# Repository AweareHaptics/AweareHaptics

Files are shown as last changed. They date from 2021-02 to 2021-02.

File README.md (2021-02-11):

# AweareHaptics

Nowadays, the french population amounts more than 207 000 blind people and more than a million people suffer from visual defficiencies. According to the OMS, the number of visually impaired people should triple by 2050. Currently, the support tools developed and available for these people are not technologically advanced and often require significant purchase costs. We therefore decided to develop a tool to help with spatial orientation, accessible to all, for the blind or visually impaired.

**Aweare Haptics is an open source project on the development of a haptic vest allowing the blind or visually impaired to orient themselves in their surrounding environment.**

Aweare Haptics is a student project in partnership with the CRI.

This readme is a comprehensive guide on how to use the Git so you can build the vest for yourself. It also contains explainations on our choices so you can adapt it for yourself.

### Requirements

List of hardware required to get started with your project:

- 3D printer
- Soldering station
- Sewing station

# Synopsis

The haptic vest is composed of infrared sensors to detect obstacles, 2 movuinos to transfer instructions to the motor actuators sewn to the vest. The location of the vibrators was determined by performing a sensitivity mapping. 

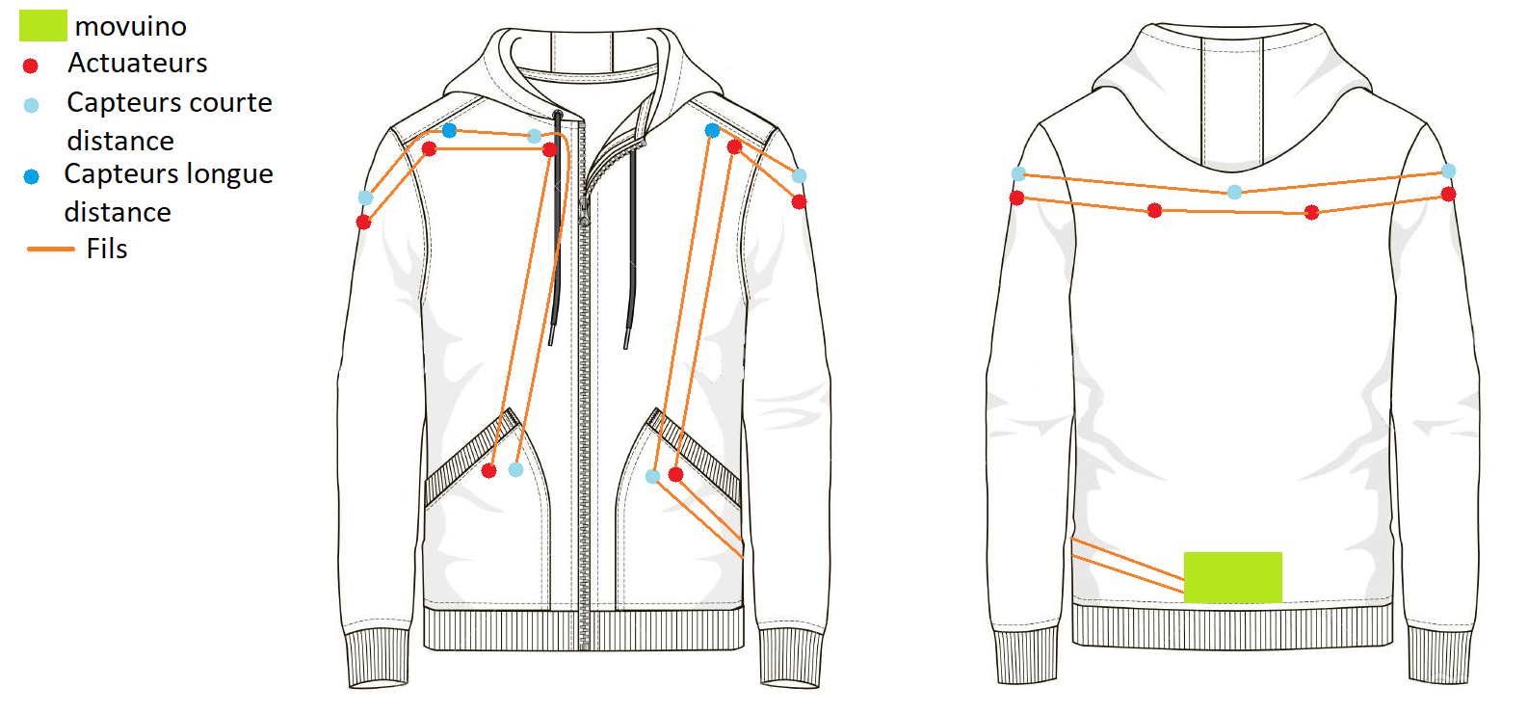
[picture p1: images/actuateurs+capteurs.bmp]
Haptic Vest wiring and components position


# Brief

The vest will be entirely made by you. This guide will give you the different components we used to make our own vest. If at any point in the process of building it, you think that something we made isn't adapted for you, don't hesitate to customize it. This repository is mostly a guideline to help you along the way. We will explain our thought process so you can better understand our choices.

The Vest in itself is made in 2 separate parts. Each part is controlled by one movuino board. The first one is the motor control. 

# Architecture of this repository

This repository is divided into multiple folders :

## 3D Model

In this folder you will find two other folders. They include the 3D model that we use to make the vest :

- "Holders" contains the ones used to support the sensors in the vest

- "Caps" contains the ones used to encapsulate the vibration motor.

## Code 

This folder is composed of two folders :
- "Motors" contains the code to upload to the movuino that operates the motors
- "Sensors" contains the code to upload to the movuino that operates the sensors

The code manages the wifi connection. The motor part takes care of setting up the server whereas the sensors represent the hotspot/client.

#  Motor Actuators

## Required hardware

For every motor used you'll need the following components:
- Néomotor PCB: you can find our brd file in the repository
- SMD resistor 10Ω type 0805 : link to [manufacturer reference : CRCW080510R0FKEA](https://fr.rs-online.com/web/p/resistances-cms/6790825/)
- SMD resistor 100Ω type 0805 : link to [manufacturer reference : CR0805-FX-1000ELF](https://fr.rs-online.com/web/p/resistances-cms/7408978/)
- SMD resistor 442Ω type 0805 : link to [manufacturer reference : ERA6AEB4420V](https://fr.rs-online.com/web/p/resistances-cms/7086023/)
- SMD resistor 4KΩ type 0805 : link to [manufacturer reference : CRCW08054K02FKEA](https://fr.rs-online.com/web/p/resistances-cms/6791471/)
- Capacitor type 104 : 10nF, SMD type 0805 :  link to  [manufacturer reference : CC0805KRX7R9BB103](https://fr.rs-online.com/web/p/condensateurs-ceramique-multicouches/4614013/)
- Transitor npn SOT-32 :  link to  [manufacturer reference : MMBT3904LT1G](https://fr.rs-online.com/web/p/transistors-bipolaires-bjt/5450343/)
- Vibration Motor [Type Model NFP-P0716](https://nfpshop.com/product/7mm-vibration-motor-16mm-type-model-nfp-p0716-3v-12000rpm-7-3g-amplitude)

## Setting up the PCB

You'll need to order or make your own PCB with the brd file found on this repository to make the motors work.

## Mounting/Assembly

## Wiring
 - Connect the GND pin of the movuino to the IN GND pin of the pcb
 - Connect the +5V pin of the movuino to the IN +5V pin of the pcb
 - Connect the +3V pin of the movuino to the IN +3V pin of the pcb
 - Connect the D9 pin of the movuino to the IN DIN pin of the pcb
 - Connect the two motor wires to the motor labeled pins on the pcb (in whatever order as the motor isn't polarized)

Then connect :
 - The OUT GND of the first pcb to the following pcb on its IN GND pin
 - The OUT +5V of the first pcb to the following pcb on its IN +5V pin
 - The OUT +3V of the first pcb to the following pcb on its IN +3V pin
 - The DOUT pin of the first pcb to the DIN of the following pcb 

## Code 

Upload the source code to the movuino

The movuino card becomes a sever socket on the address 192.168.4.2
A maximum of one client can connect at a time : this can be changed in the file : ... define BN_CLIENT // TODO ADD NAME OF FILE

The server receives messages from the clients. The messages need to be formated in strings containing the id of the vibration motor that we want to pilot along with its intensity whose value ranges from 0 to 3

## Solder the PCB

The motors PCB are made to all be in series of one another. The first PCB has its 3.3V to the 3 Volts battery. The 5V is connected to the movuino's 5V. Then the DIN is connected to the D4 pin of the movuino. The ground is conected to the shared ground of the movuino and the 3V battery.

For the I/Os of the other PCB, the OUT first board is directly linked to the IN of the second board. The OUT of the second is connected to the IN of the third and continue until all your motor controller are linked. The OUT of the last board doesn't need to be connected anywhere.

For the Motor pins, you just need to connect them to a exentric mass vibration motor. They can be wired in both direction.

For each PCB you also have to solder the resistors, capacitor, transistor and the microcontroller.

### soldering the passive components :

R1 is the 400 Ohms resistor.
R2 is the 4K Ohms resistor.
R3 is the 100 Ohms resistor.
R4 is the 10 Ohms resistor.
C1 is the capacitor.

### soldering the Microcontroller :

To solder the MicroController you have to put the tiny hole such as it is facing you and in the top left. Then you can solder it to the board. 

## Mounting

# Infrared Sensors

## Required hardware

- Prototyping plate : link to [manufacturer reference  : 743635] https://fr.rs-online.com/web/p/cartes-matrices/4853892/
- Infrared sensor VL53L0X TECNOIOT (measures up to 2 meters) : link to [manufacturer reference : A513-VL53L0X-297-5PCS ]
https://www.amazon.fr/TECNOIOT-VL53L0X-Flight-Distance-GY-VL53L0XV2/dp/B084BTP479/ref=sr_1_6?__mk_fr_FR=%C3%85M%C3%85%C5%BD%C3%95%C3%91&crid=6Q645XXPDDA7&dchild=1&keywords=lidar+arduino&qid=1606946373&sprefix=lidar+%2Caps%2C326&sr=8-6
- Infrared sensor VL53L1X STMicroelectronics (measures up to 4 meters): link to [manufacturer reference : VL53L1X-SATEL] https://fr.rs-online.com/web/p/modules-de-developpement-pour-capteurs/1827794/?cm_mmc=FR-PPC-DS3A-_-bing-_-3_FR_FR_Modules+de+d%C3%A9veloppement+pour+capteurs_STMicroelectronics_Exact-_-STMicroelectronics+-+Modules+de+d%C3%A9veloppement+pour+capteurs+-+1827794-_-vl53l1x+satel&matchtype=e&kwd-71743717917902:loc-66&gclid=534000e661d01b55fc8760f1bc5fa77a&gclsrc=3p.ds&msclkid=534000e661d01b55fc8760f1bc5fa77a

## Setting up the prototyping plate

Solder a line for 5V, a line for GND, a line for SCL and a line for SDA.

## Mouting/Assembly

## VLX53L0X pins

### Board description

Take the board with its captor facing you and in the right side of the board. The pins are in the left side. From top to bottom we have :

- Vin 
- Ground
- SCL
- SDA
- GPIO1 (unused for this project)
- XSHUT

## VLX53L1X pins

Schematics for the VL53L1X corresponding pins :

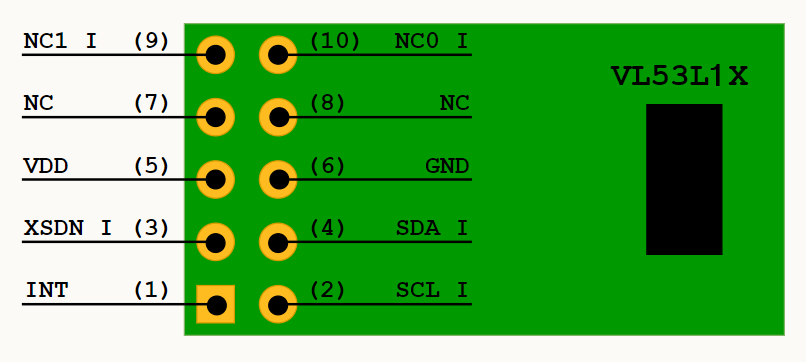
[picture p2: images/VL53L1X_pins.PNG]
VL53L1X pins


### Schematic description

Take the board with its captor facing you and in the right side of the board. The pins are in the left side. The most bottom left is the INT pin, it is unused for this project. The one above the INT pin is the XSDN pin. Above the XSDN pin is the Vdd pin. Right to Vdd is the ground pin. Below the ground you have the SDA pin. And below SDA is SCL. All other pin are unused.

## Wiring

### Wiring schematic :

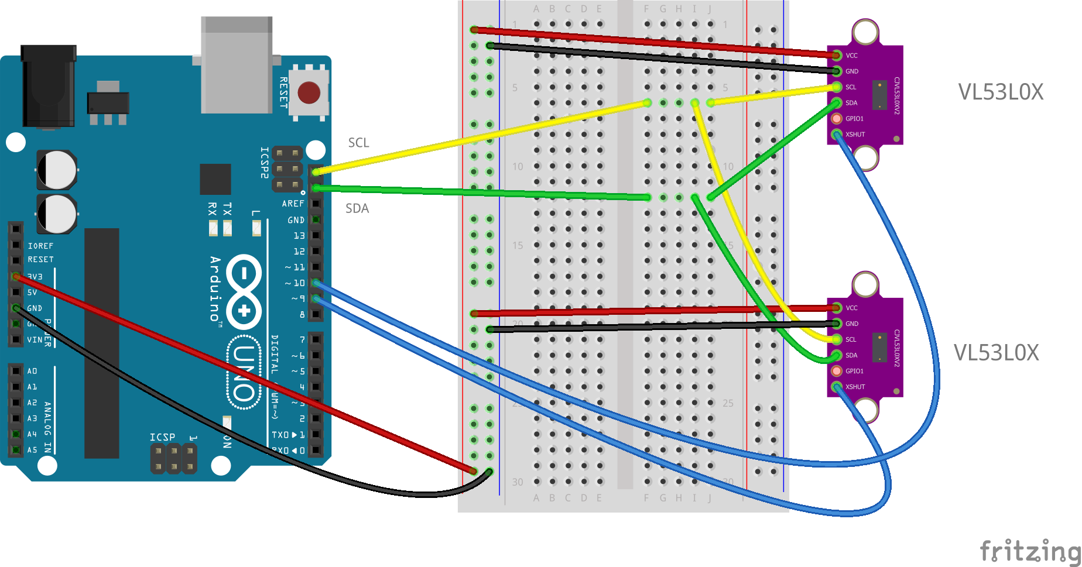
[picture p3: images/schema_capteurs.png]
Schematics sensor


### Schematic description

 - Connect the GND pin of the movuino to any line on the prototyping plate which becomes its designated line. (GND)
 - Connect the +3V pin of the movuino to any line on the prototyping plate which becomes its designated line. (+3V)
 - Connect the SCL pin of the movuino to any line on the prototyping plate which becomes its designated line. (SCL)
 - Connect the SDA pin of the movuino to any line on the prototyping plate which becomes its designated line. (SDA)

Connect then for every sensor:

 - Connect the GND pin of the sensor to the desigLnated GND line on the prototyping plate
 - Connect the VIN/VDD pin of the sensor to the designated +3V line on the prototyping plate
 - Connect the SCL pin of the sensor to the designated SCL line on the prototyping plate
 - Connect the SDA pin of the sensor to the designated SDA line on the prototyping plate
 - Connect the pins D3, D4, D5... of the movuino to the XSHUT pin for the sensor VL53L0X or XSDN pin for the VL53L1X sensor.

## Code 

# Sensibility protocole

Sensibility mapping process:

Before getting started with the mapping, you'll need to prepare your work environment.
You'll need to carry out the protocole by using the body proportions of the person wearing the vest.
You'll need to use a vibration motor connected to a power source of 3.3V to map out the sensitive areas of the person's body.

## First step : Divide into squares the person's body

We'll seperate the torso, the back and the arms into different testing areas.

 -On the torso : seperate in 10 different areas
 --Area 1 and 2 : Upper left and right part of the torso 
 --Area 3 and 4 : left and right part of the chest
 --Area 5 and 6 : left and right part of the ribs under the chest area
 --Area 7 and 8 : left and right part of the belly
 --Area 9 and 10 : left and right part of the hips

 -On the back : seperate in 8 different areas.
 --Area 1 and 2 : left and right part of the shoulder blades
 --Area 3 and 4 : left and right part of the ribs under the shoulder blades
 --Area 5 and 6 : left and right part of lower back (lumbar region)
 --Area 7 and 8 : left and right part of hips

 -On the arms : seperate in 4 different areas
 --Area 1 : right shoulder
 --Area 2 : right arm 
 --Area 3 : left shoulder
 --Area 4 : left arm 

## Second step : Mapping out the sensitive areas

- Start by powering up the motor with a voltage of 3.3V.
WARNING : In order for the mapping to be correct, the motor needs to be supplied with a constant voltage of 3.3V for the duration of the tests.

-In order to familiarize yourself with the feeling of the vibrating motor, try out every area at least once before ruling out the ones that are too sensitive.

-Position the motor on every testing area and define one of the following feedback:
--Extremely sensitive area : red
--Sensitive area : orange
--Not very sensitive area : yellow
--Not recommended area (private regions or no sensitivity) : white

-We recommend repeating the protocole multiple times for better results.

# Authors

* [**Guicharnaud Léo**](https://github.com/Lightman31)
* [**Buot Adrien** ](https://github.com/Bubu781 )
* [**terre Mikhali** ](https://github.com/Mikhali)
* [**Sabatey Clara** ](https://github.com/clarasbty)
* [**Noiraux Coline** ](https://github.com/NoireauxColine)
* [**Beurotte Marine** ](https://github.com/mama98)

# Version Francaise :

De nos jours, on compte parmis la population française plus de 207 000 aveugles et plus d’1 million de personnes souffrant de cécité visuelle. De plus, d’après l’OMS, le nombre de malvoyants pourrait trippler d’ici 2050. Actuellement, les outils d’aide développés pour ces personnes sont peu avancés technologiquement et nécessite souvent d’important coût d’achat. Nous avons donc décidé de développer un outil d’aide à l’orientation dans l’espace accessible à tous pour les personnes aveugles et malvoyantes.

**Aweare Haptics est une veste haptique open source permettant aux personnes aveugles et malvoyantes de s’orienter dans leur environnement.**

# Pour commencer

Entrez ici les instructions pour bien débuter avec votre projet...

### Pré-requis

Ce qu'il est requis pour commencer avec votre projet du point de vue du matériel

- Imprimante 3D
- Poste de soudure
- Poste de couture

# Démarrage

Notre veste sera composée de capteurs infrarouge pour détecter la présence d’obstacle et de movuino pour transmettre l’information aux actuateurs présent sur la veste. L’emplacement des vibreurs a été déterminés par la réalisation d’une cartographie de sensibilité.

Veste haptique branchement et placement des composants

#  Partie moteurs actuateurs

## Matériel

Pour chaque moteur vous aurez besoin de :

- faire faire un pcb néomotor : le fichier brd est dans le repo
- résistance 10Ω boitier 0805 : lien vers la [référence fabriquant : CRCW080510R0FKEA](https://fr.rs-online.com/web/p/resistances-cms/6790825/)
- résistance 100Ω boitier 0805 : lien vers la [référence fabriquant : CR0805-FX-1000ELF](https://fr.rs-online.com/web/p/resistances-cms/7408978/)
- résistance 442Ω boitier 0805 : lien vers la [référence fabriquant : ERA6AEB4420V](https://fr.rs-online.com/web/p/resistances-cms/7086023/)
- résistance 4KΩ boitier 0805 : lien vers la [référence fabriquant : CRCW08054K02FKEA](https://fr.rs-online.com/web/p/resistances-cms/6791471/)
- Condensateur type 104 : 10nF, boitier 0805 : lien vers la [référence fabriquant : CC0805KRX7R9BB103](https://fr.rs-online.com/web/p/condensateurs-ceramique-multicouches/4614013/)
- transitor npn simple boitier SOT-32 : lien vers la [référence fabriquant : MMBT3904LT1G](https://fr.rs-online.com/web/p/transistors-bipolaires-bjt/5450343/)
- moteur vibrant [Type Model NFP-P0716](https://nfpshop.com/product/7mm-vibration-motor-16mm-type-model-nfp-p0716-3v-12000rpm-7-3g-amplitude)

## Fabrication du pcb

vous aurez besoin de commander ou bien de fabriquer des PCB, pour bien faire fonctionner les moteurs vibrant

## Montage

AJOUTER SCHEMA

## Branchements
 - brancher le GND de la movuino sur le GND du pcb
 - brancher le +5V de la movuino sur le +5V du pcb
 - brancher le +3V de la movuino sur le +3V du pcb
 - brancher la pin D9 de la movuino sur le DIN du pcb
 - brancher les deux fils sur moteur sur le bornes moteur du pcb. (le moteur n'est pas polarisé)

brancher ensuite :
 - le GND du pcb sur le GND du pcb suivant
 - le +5V de pcb sur le +5V du pcb suivant
 - le +3V de pcb sur le +3V du pcb suivant
 - la pin D9 de pcb sur le DIN du pcb suivant

## Code 

téléverser le code source sur la movuino

la carte movuino devient un serveur socket sur l'adresse 192.168.4.2
1 client max peut s'y connecter : ce nombre est modifiable dans le fichier ... : le define BN_CLIENT // TODO : dire le nom du fichier  

le serveur ne fait que recevoir des messages des clients. le message doit etre formaté un string cntenant le numéo de l'actuateur à faire vibrer, ainsi qu'une intensité ayant une valeur comprise entre 0 et 3 

## Souder les PCBd

## Monter..

#  Partie capteurs infrarouge

## Matériel

- Plaque de prototypage : lien vers la [référence fabriquant : 743635] https://fr.rs-online.com/web/p/cartes-matrices/4853892/
- Capteur infrarouge VL53L0X TECNOIOT (mesure jusqu'à 2m) : lien vers la [référence fabriquant : A513-VL53L0X-297-5PCS ]
https://www.amazon.fr/TECNOIOT-VL53L0X-Flight-Distance-GY-VL53L0XV2/dp/B084BTP479/ref=sr_1_6?__mk_fr_FR=%C3%85M%C3%85%C5%BD%C3%95%C3%91&crid=6Q645XXPDDA7&dchild=1&keywords=lidar+arduino&qid=1606946373&sprefix=lidar+%2Caps%2C326&sr=8-6
- Capteur infrarouge VL53L1X STMicroelectronics (mesure jusqu'à 4m): lien vers la [référence fabriquant : VL53L1X-SATEL] https://fr.rs-online.com/web/p/modules-de-developpement-pour-capteurs/1827794/?cm_mmc=FR-PPC-DS3A-_-bing-_-3_FR_FR_Modules+de+d%C3%A9veloppement+pour+capteurs_STMicroelectronics_Exact-_-STMicroelectronics+-+Modules+de+d%C3%A9veloppement+pour+capteurs+-+1827794-_-vl53l1x+satel&matchtype=e&kwd-71743717917902:loc-66&gclid=534000e661d01b55fc8760f1bc5fa77a&gclsrc=3p.ds&msclkid=534000e661d01b55fc8760f1bc5fa77a

## Elaboration de la plaque de prototypage 

METTRE PHOTO DE LA PLAQUE

faire une ligne 5V, une ligne GND, une ligne SCL et une ligne SDA

## Montage

Schema Capteur

Schema des pins du VL53L1X :
VL53L1X pins

## Branchements

 - brancher le GND de la movuino sur une ligne de la plaque 
 - brancher le +3V de la movuino sur une ligne de la plaque 
 - brancher la pin SCL de la movuino sur une ligne de la plaque
 - brancher la pin SDA de la movuino sur une ligne de la plaque

brancher ensuite pour chaque capteurs :

 - brancher la pin GND du capteur a la ligne GND de la plaque
 - brancher la pin VIN/VDD du capteur a la ligne 3V de la plaque
 - brancher la pin SCL du capteur a la ligne SCL de la plaque
 - brancher la pin SDA du capteur a la ligne SDA de la plaque
 - brancher la pin D3, D4, D5... de la movuino sur le XSHUT des capteurs VL53L0X ou XSDN pour les capteurs VL53L1X.

## Code 

# Protocole de sensibilité

Processus de réalisation de la cartographie:

Avant de commencer la cartographie, il faut préparer l'environnement de travail.
Ce protocole est à réaliser sur le corps de la personne qui portera la veste.
Pour réaliser ce protocole, il faut se munir d'un moteur vibrant branché à une puissance de 3,3V.

## Première étape : Qadriller le corps de la personne 

Nous allons séparer le buste, le dos et les bras en différentes zones à tester.

-Sur le devant du corps : séparer en 10 zones.
--Zone 1 et 2 : Haut du buste partie droite et partie gauche
--Zone 3 et 4 : Poitrine partie droite et partie gauche
--Zone 5 et 6 : Cotes sous poitrine partie droite et partie gauche
--Zone 7 et 8 : Ventre partie droite et partie gauche
--Zone 9 et 10 : Hanches partie droite et partie gauche

-Sur le derrière du corps : séparer en 8 zones.
--Zone 1 et 2 : Omoplates partie droite et partie gauche
--Zone 3 et 4 : Cotes sous omoplates partie droite et partie gauche
--Zone 5 et 6 : Bas du dos (zone lombaire) partie droite et partie gauche
--Zone 7 et 8 : Hanches partie droite et partie gauche

-Sur les bras : séparer en 4 zones 
--Zone 1 : bras droit épaule
--Zone 2 : bras droit haut du bras
--Zone 3 : bras gauche épaule
--Zone 4 : bras gauche haut du bras

## Deuxième étape : Elaboration de la cartographie

-Commencer par allumer le moteur avec une puissance de fonctionnement de 3,3V.
ATTENTION : Pour que la cartographie soit efficace, le moteur doit rester à 3,3V pendant tout le test.

-Passer une première fois le moteur sur l'ensemble des zones pour se familiariser avec le ressenti des vibrations.

-Positionner ensuite le moteur sur chaque zone à tester et définir un ressenti prédéfini:
--Zone fortement sensible : Zone Rouge
--Zone sensible : Zone Orange
--Zone peu sensibe : Zone Jaune
--Zone déconseillée (mauvais placement ou aucune sensibilité) : Zone Blanc

-Nous vous conseillons de le faire plusieurs fois pour des résultats adaptés.

# Auteurs

* [**Guicharnaud Léo**](https://github.com/Lightman31)
* [**Buot Adrien** ](https://github.com/Bubu781 )
* [**terre Mikhali** ](https://github.com/Mikhali)
* [**Sabatey Clara** ](https://github.com/clarasbty)
* [**Noiraux Coline** ](https://github.com/NoireauxColine)
* [**Beurotte Marine** ](https://github.com/mama98)

## Versions 
Liste des versions : [**Cliquer pour afficher les tags**](https://github.com/AweareHaptics/AweareHaptics/tags)

## Fabriqué avec

- [Arduino](https://www.arduino.cc/) - IDE
- [VScode](https://code.visualstudio.com/) + [PlatformIO](https://platformio.org/) - éditeur de texte et IDE
- [Fusion360](https://www.autodesk.fr/products/fusion-360/overview) - logiciel de modélisation 3D 
- [Eagle](https://www.autodesk.fr/products/eagle/overview) - logiciel de conception électronique

## License
Ce projet est sous licence ``exemple: WTFTPL`` - voir le fichier [LICENSE.md](LICENSE.md) pour plus d'informations

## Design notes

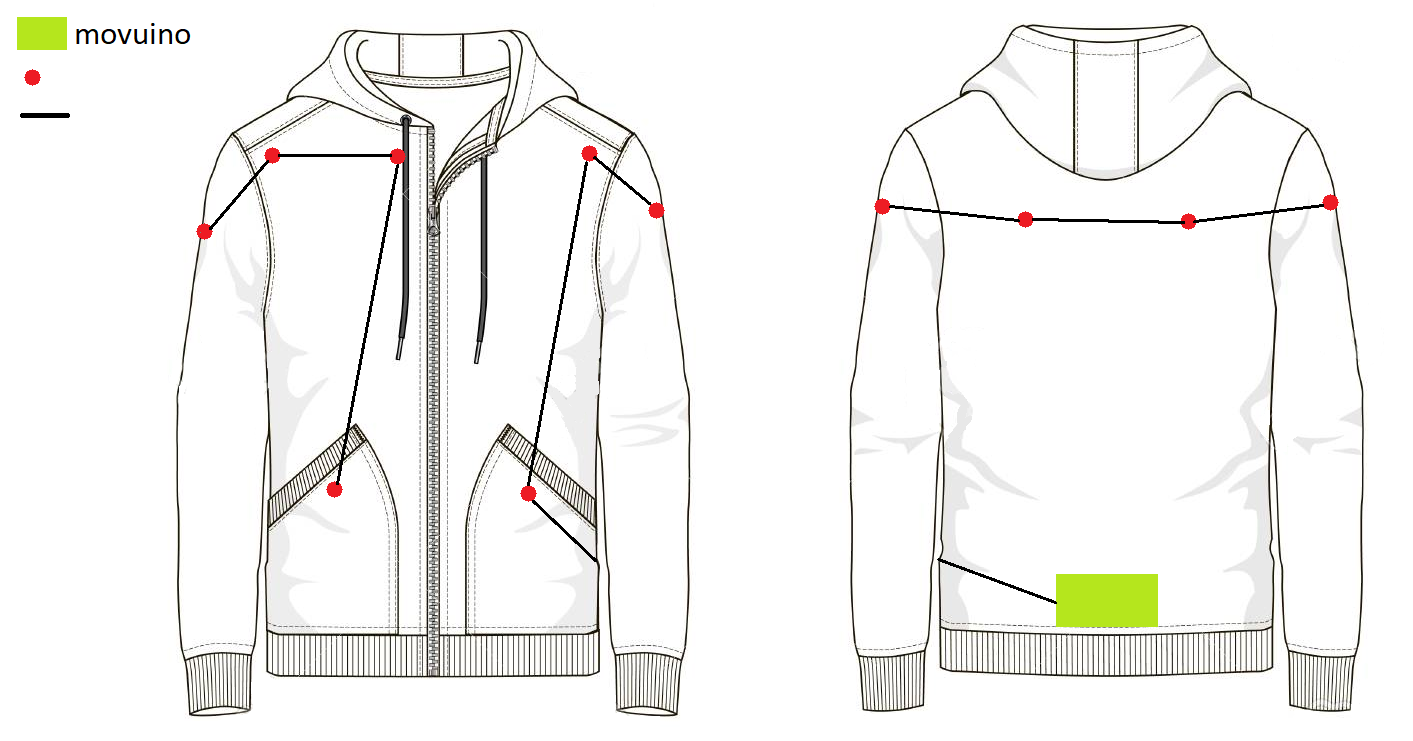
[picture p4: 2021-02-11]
images/actuateurs1.bmp

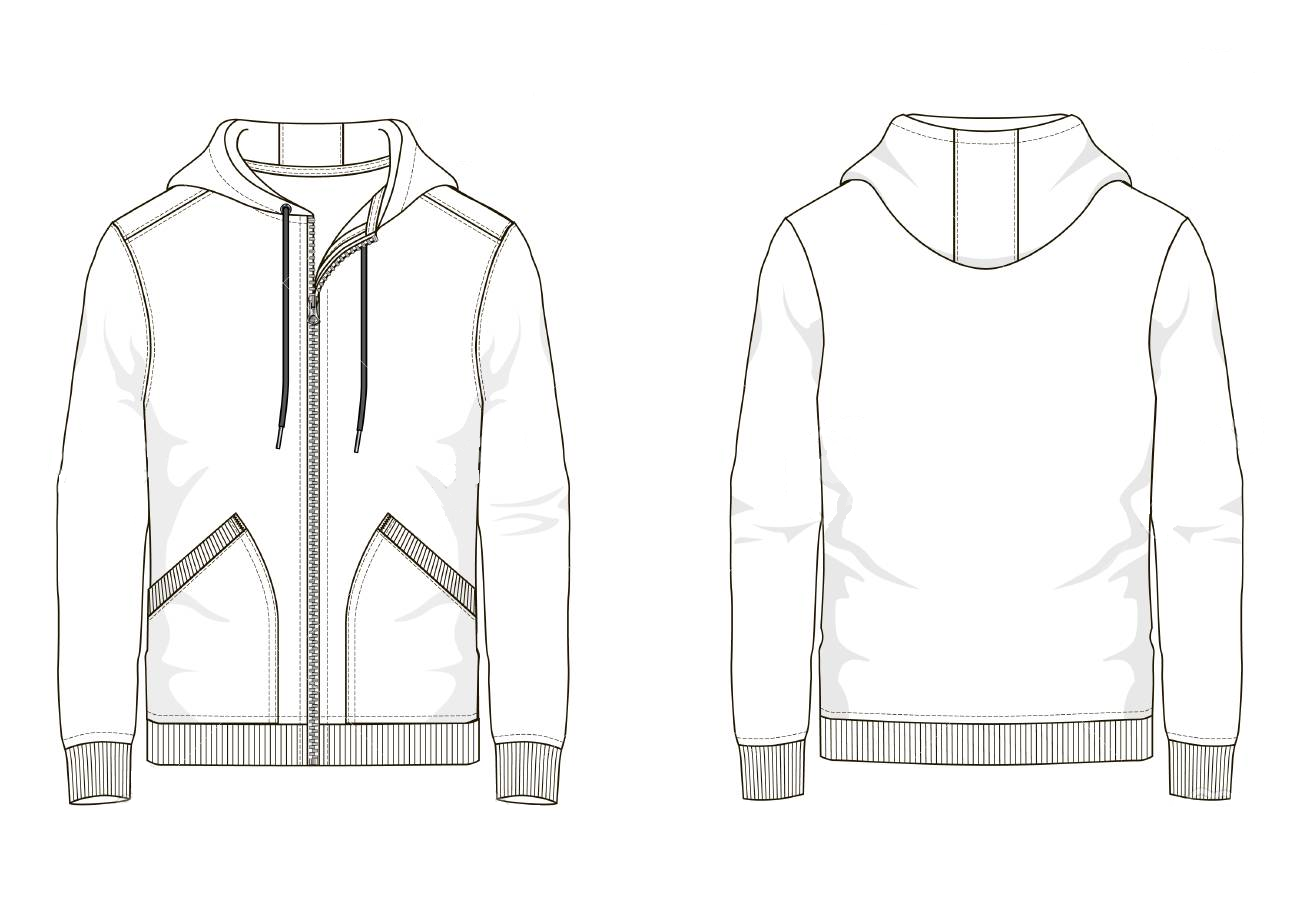
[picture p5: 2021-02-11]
images/actuateurs.bmp

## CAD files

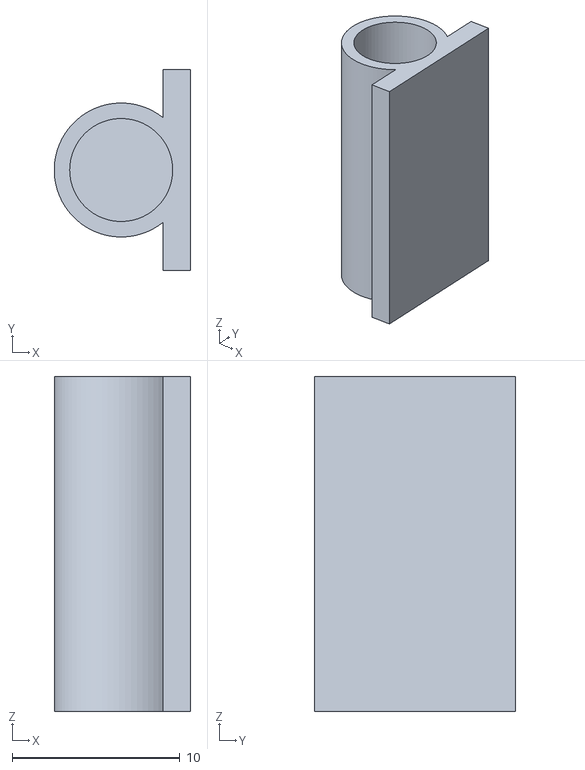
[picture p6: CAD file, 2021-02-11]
modeles 3D/capsule_moteur_vibrant_6_16mm v2.stl
8.15 x 12.0 x 20.0

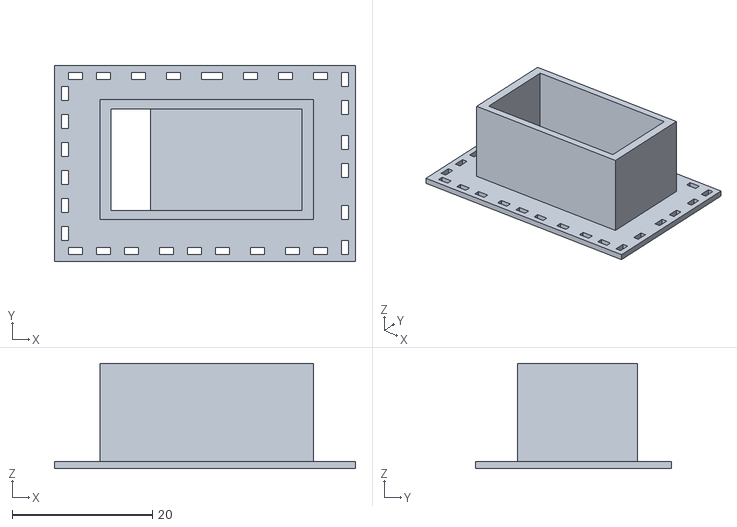
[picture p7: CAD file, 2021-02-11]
modeles 3D/support_capteur_4m.stl
43.0 x 28.0 x 15.0

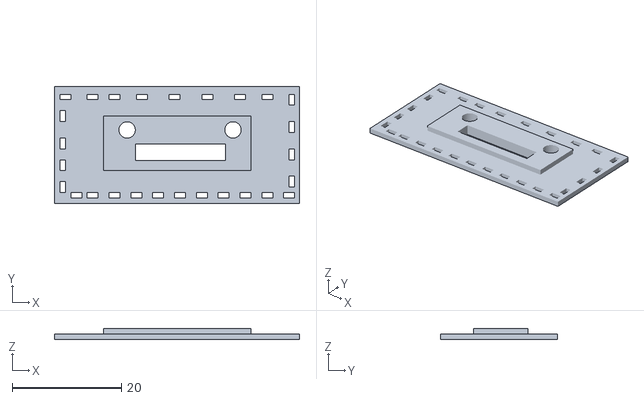
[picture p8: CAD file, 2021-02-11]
modeles 3D/support_capteur_1m_incliné.stl
44.9 x 21.4 x 2.00

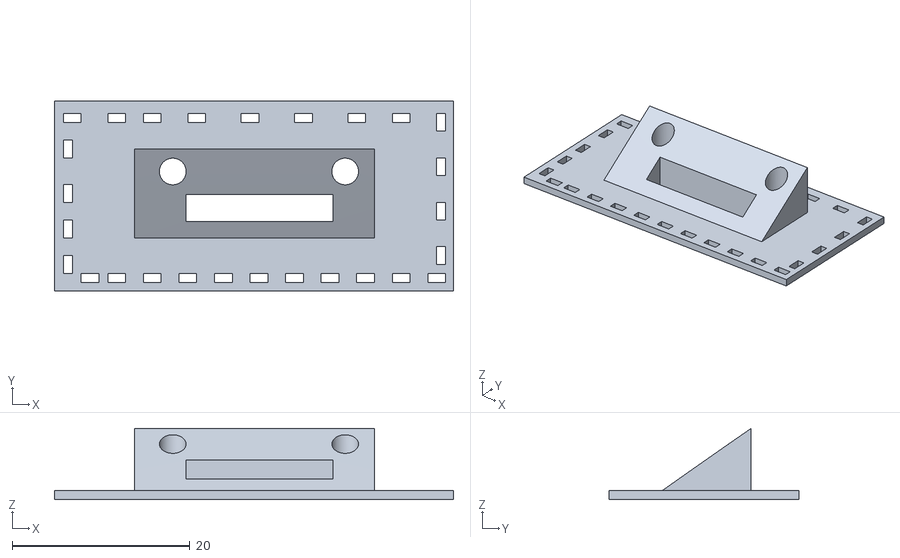
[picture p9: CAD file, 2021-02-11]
modeles 3D/support_capteur_1m.stl
44.9 x 21.4 x 8.00

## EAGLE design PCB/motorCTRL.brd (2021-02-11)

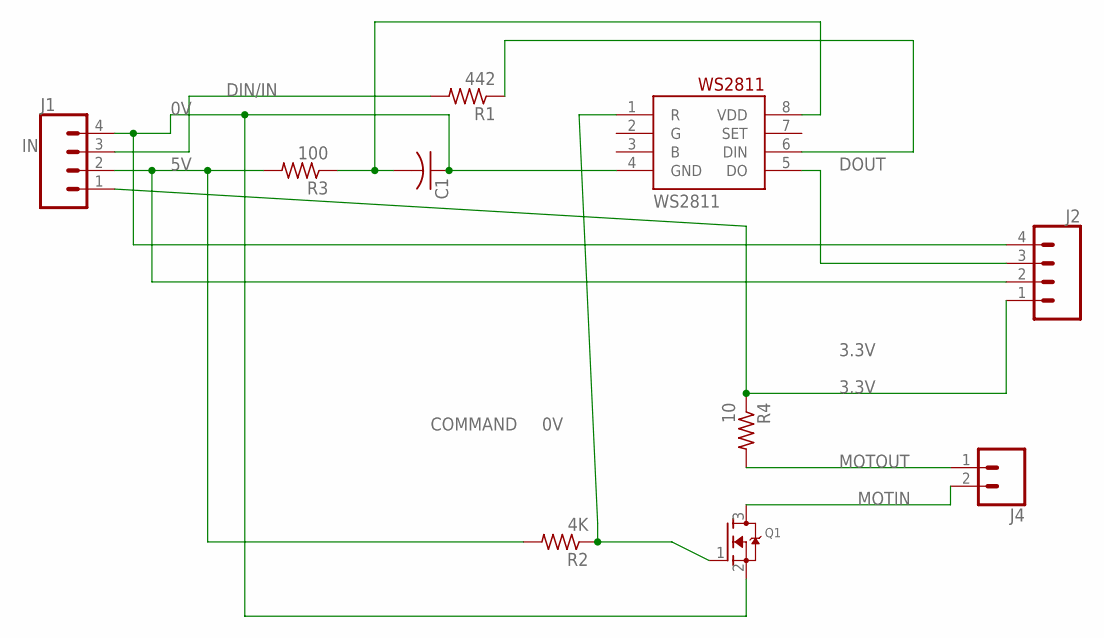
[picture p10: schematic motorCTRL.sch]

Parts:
C1: C-USC0805; C0805
J1, J2: CONN_04; 1X04
J4: CONN_02; 1X02
Q1: MOSFET-NREFLOW; SOT23
R1: 442; R0805
R2: 4K; R0805
R3: 100; R0805
R4: 10; R0805
WS2811: WS2811-SOP8; SO08-SKINNYPADS

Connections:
0V: C1.1, J1.4, J2.4, Q1.2 (S), WS2811.4 (GND)
3.3V: J1.1, J2.1, R4.1
5V: J1.2, J2.2, R2.2, R3.2
COMMAND: Q1.1 (G), R2.1, WS2811.1 (R)
DIN/IN: J1.3, R1.2
DOUT: J2.3, WS2811.5 (DO)
MOTIN: J4.2, Q1.3 (D)
MOTOUT: J4.1, R4.2
unnamed: R1.1, WS2811.6 (DIN)
VCC: C1.2, R3.1, WS2811.8 (VDD)

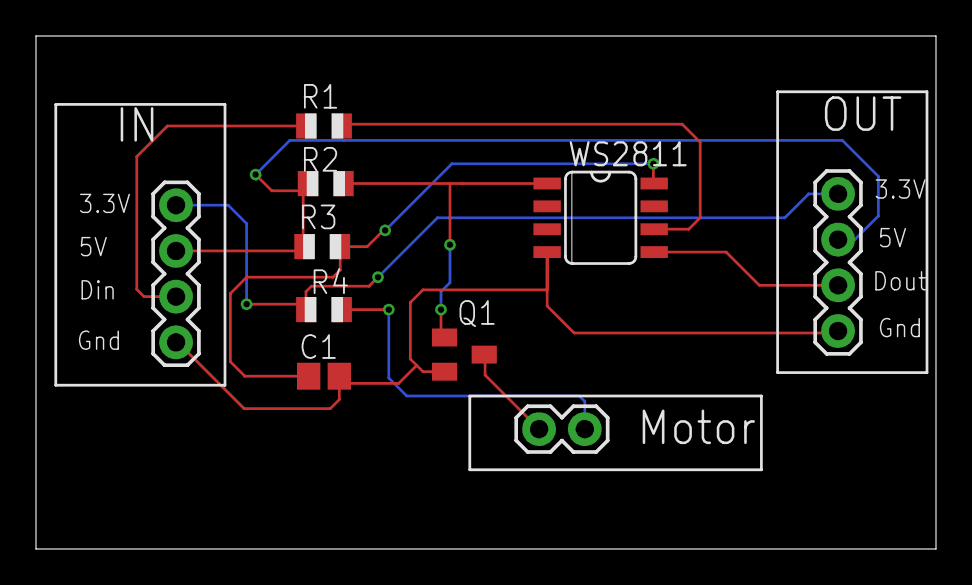
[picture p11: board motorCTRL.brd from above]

Board: 2 copper layers, 50.0 x 28.5 mm, 10 parts (0 on the bottom side), 10 nets.

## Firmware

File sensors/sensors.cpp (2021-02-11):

#include "sensors.hpp"

/*
*   Functions commons to all classes
*/

// Constructor of sensor, we initialize the variables
Sensor::Sensor(int id, int pin, int address){
    this->id = id;
    this->pin = pin;
    this->address = address;
    Serial.print("sensor id:");
    Serial.println(this->id);
}

// setClient We set the client to send the update of the sensors
void Sensor::setClient(WiFiClient client){
    this->client = client;
}

// setState we change the state of the sensor and send the information
void Sensor::setState(typeState_t state){

      Serial.print("  id : ");
      Serial.println(this->id);
      Serial.print("  state : ");
      Serial.println(state);
    this->state = state;
    this->sendToActuator();
}

// sendToActuator we send a string to the client, to tell the actuator the action they should do
void Sensor::sendToActuator(){
  uint8_t data[2];
  data[0] = this->id;
  data[1] = this->state;
    if(this->client.connected()>0)
        this->client.write(data,2);
  /*Serial.print("data0:");
  Serial.println(data[0]);
  Serial.print("data1:");
  Serial.println(data[1]);*/
  
}

/*
*   Functions concerning the short sensors
*/

SensorShort::SensorShort(int id, int pin, int address) : Sensor(id, pin, address){
    pinMode(this->pin, OUTPUT);
    digitalWrite(this->pin, LOW);  
    delay(10); 
    digitalWrite(this->pin, HIGH);
    delay(10);
    digitalWrite(this->pin, LOW);
    delay(10);
}

void SensorShort::init(){
    digitalWrite(this->pin, HIGH);
    if(!this->lox.begin(this->address)) {
        Serial.println("Failed to boot a VL53L0X");
        Serial.println(this->pin);
        while(1);
    }
    delay(10);
}

void SensorShort::readSensor(){
    VL53L0X_RangingMeasurementData_t measure;
    this->lox.rangingTest(&measure, false); // pass in 'true' to get debug data printout!
    if(measure.RangeStatus != 4) {
        if(measure.RangeMilliMeter >= 20 && measure.RangeMilliMeter <= 430 && this->state != HIGHENERGY){
            this->setState(HIGHENERGY);
        }else if(measure.RangeMilliMeter > 430 && measure.RangeMilliMeter <= 840 && this->state != MEDIUMENERGY ){
            this->setState(MEDIUMENERGY);
        }else if(measure.RangeMilliMeter > 840 && measure.RangeMilliMeter < 1270 && this->state != LOWENERGY){
            this->setState(LOWENERGY);
        }else if(measure.RangeMilliMeter > 1270 && this->state != IDLE){
            this->setState(IDLE);
        }
    //Serial.print("distance court n° ");
    //Serial.print(this->pin);
    //Serial.print(" : ");
    //Serial.println(measure.RangeMilliMeter);
    }else if(this->state != IDLE){
        this->setState(IDLE);
    }
}

SensorLong::SensorLong(int id, int pin, int address) : Sensor(id, pin, address){
    this->distanceSensor = SFEVL53L1X(Wire, this->pin);
    Wire.begin();
    this->distanceSensor.sensorOff();
}

void SensorLong::init(){
  this->distanceSensor.sensorOn();
  this->distanceSensor.setI2CAddress(this->address);

  if (this->distanceSensor.begin() != 0) //Begin returns 0 on a good init
  {
    Serial.println("Sensor failed to begin. Please check wiring. Freezing...");
    Serial.println(this->pin);
    while(1);
  }

  this->distanceSensor.setDistanceModeLong();
  Serial.println(this->distanceSensor.getI2CAddress());
}

void SensorLong::readSensor(){
  this->distanceSensor.startRanging(); //Write configuration bytes to initiate measurement
  while (!this->distanceSensor.checkForDataReady())
  {
    delay(1);
  }
  
  int distance = this->distanceSensor.getDistance(); //Get the result of the measurement from the sensor
  
  this->distanceSensor.clearInterrupt();
  this->distanceSensor.stopRanging();

  if(distanceSensor.getRangeStatus() == 0) // Returns 0 if no errors are found 
  { 
    Serial.print("distance long : ");
    Serial.println(distance);
    if(distance >= 40 && distance <= 1000 && this->state != HIGHENERGY){
        this->setState(HIGHENERGY);
    }else if(distance > 1000 && distance <= 1500 && this->state != MEDIUMENERGY ){
        this->setState(MEDIUMENERGY);
    }else if(distance > 1500 && distance < 2200 && this->state != LOWENERGY){
        this->setState(LOWENERGY);
    }else if(distance > 2200 && this->state != IDLE){
        this->setState(IDLE);
    }
  }else if(this->state != IDLE){
      this->setState(IDLE);
  } 
}

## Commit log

2021-01-21 premier jet des modeles
    [VL53LXX-V2_Holder v1.f3d, VL53LXX-V2_Holder v1.stl, VL53LXX-V2_Holder_V2 v1.stl, avecfondavecplaque_7.3_25_mmV1 v1.stl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]
2021-01-21 ajout des références fabriquant
2021-01-21 added the code of the server/sensors
2021-01-21 Added the child classes for the futures sensors
2021-01-25 verification de l'outil team
2021-01-25 Added long distance sensors
2021-01-31 Fixed the long range sensor idle state
2021-01-31 Add comments for SensorLong class
2021-02-01 Add instructions for the long sensors
2021-02-01 Add VL53L1X pin schematics
2021-02-02 Add code for working prototype
2021-02-02 working actuator code for prototype
2021-02-11 modèles 3D + brd et sch du PCB
    [VL53LXX-V2_Holder v1.f3d, VL53LXX-V2_Holder v1.stl, VL53LXX-V2_Holder_V2 v1.stl, avecfondavecplaque_7.3_25_mmV1 v1.stl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]

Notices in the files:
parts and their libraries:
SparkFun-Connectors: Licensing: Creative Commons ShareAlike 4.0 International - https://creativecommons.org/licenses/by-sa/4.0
